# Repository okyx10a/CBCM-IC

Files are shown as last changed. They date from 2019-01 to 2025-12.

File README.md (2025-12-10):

# CBCM-IC Testing Platform
**Full-stack mixed-signal test fixture for Charge-Based Capacitance Measurement ICs**  
Designed, fabricated, and validated at York University (2018–2019)

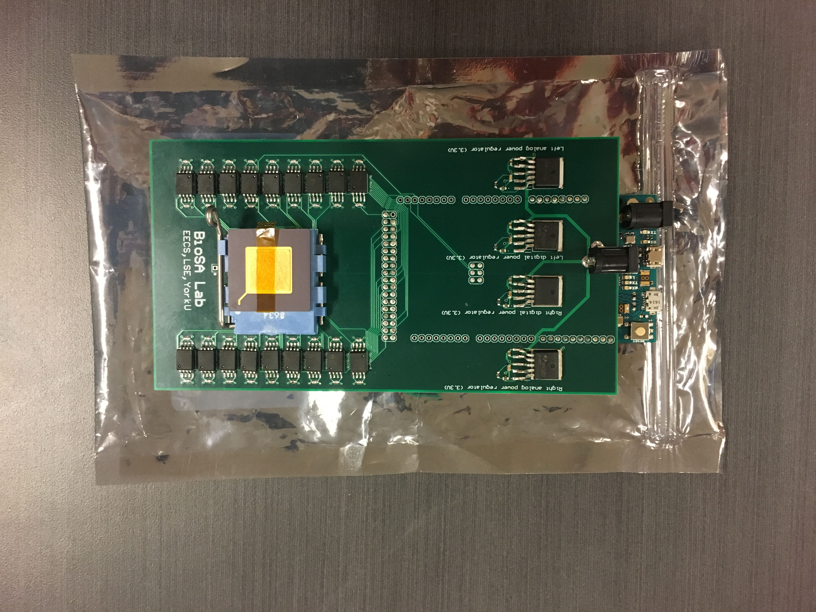
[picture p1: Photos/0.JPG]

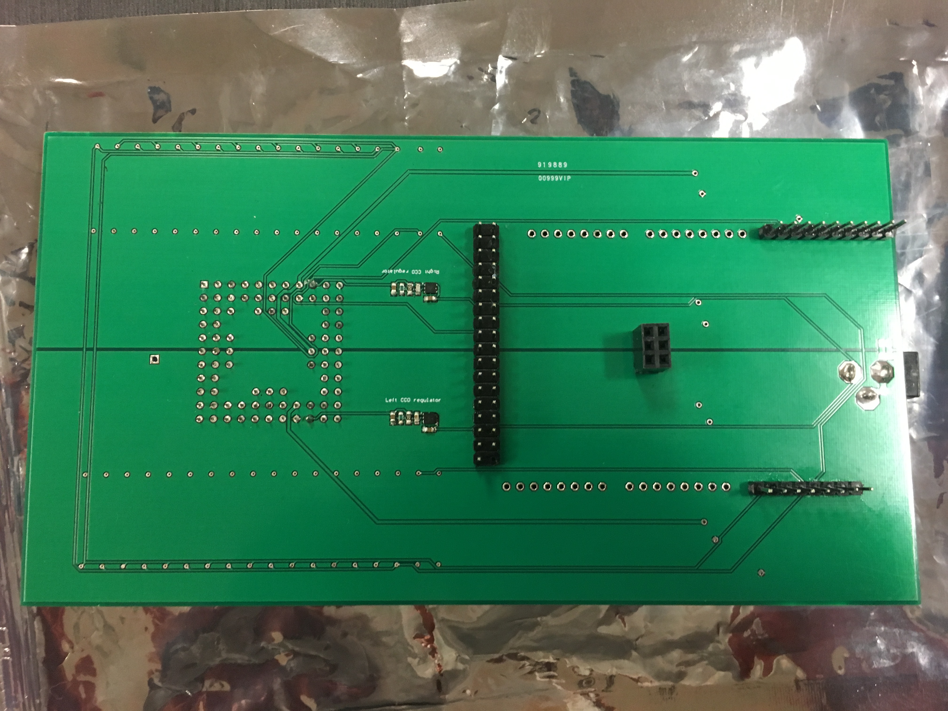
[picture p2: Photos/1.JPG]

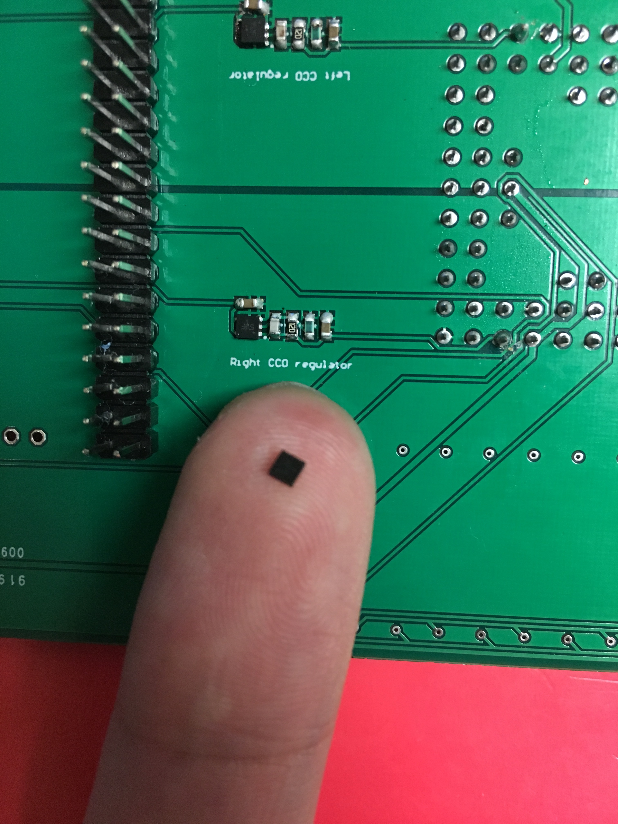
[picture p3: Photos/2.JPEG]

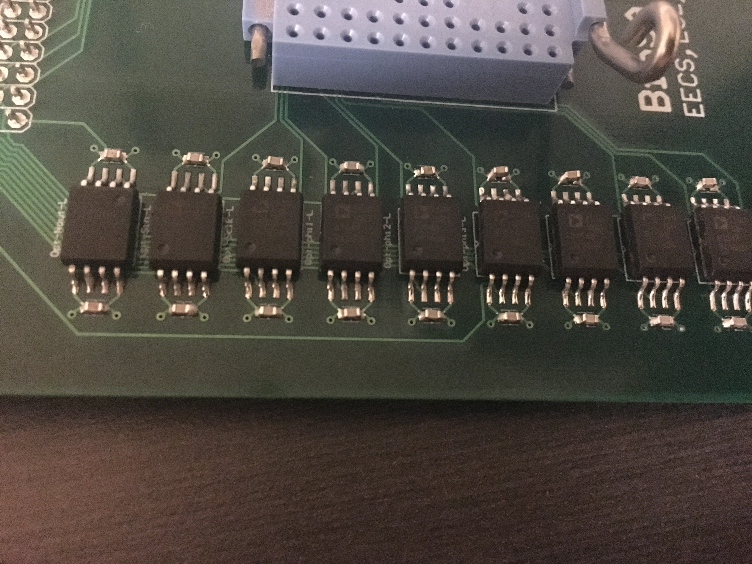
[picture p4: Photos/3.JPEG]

*4-layer mixed-signal test board with separated analog/digital ground planes*

## Directory Structure
├── Hardware/                       → Altium project  
├── Software/                       → Arduino code + PyQt GUI  
├── Photos/                         → Assembly  
├── Test results/                   → Raw data and measurement data  
├── CBCM project summery.docx       → Test fixture construction explanation  
├── Tools chain setup.txt           → Note for succeeding developer  
└── README.md

## Key Features
- 4-layer KiCad design with proper analog/digital ground splitting
- SAM3X8E ARM Cortex-M3 (Arduino Due core) for real-time pattern generation and data acquisition
- Interfaces: SPI (20 MHz), UART
- SMT soldering down to 0603 passives and QFN packages (hand-soldered prototype)
- Automated measurement and data logging via Python + PyQt GUI

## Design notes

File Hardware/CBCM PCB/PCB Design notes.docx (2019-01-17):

1. 0603 seems to be the best size for SMD prototyping.
2. EPAD pin on regulators (TO-263 package) should be connected to ground?
3. The minimal recommended capacitor is 47uF, however the selected capacitor has a (+ -20%) tolerance. Which means it might have a value lower than 47uF. Is that something I should be worried about?
4. The 1.85V regulator is untested on the breadboard I shall record every design detail.

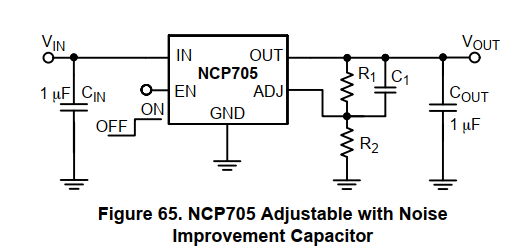
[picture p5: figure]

5. To achieve 1.85V a R2 = 99.048kOhm resistor is needed (while R1 = 130k), however only 98.8kOhm resistor is available on the market. This would result in a 1.8526V output voltage. I wonder if that 0.0026 surplus will be an issue?
6. Data sheet’s note on Cin: It is recommended to connect a minimum of 1uF Ceramic X5R or X7R capacitor close to the IN pin of the device.
7. Data sheet’s note on Cout: The NCP705 requires an output capacitor connected as close as possible to the output pin of the regulator. The minimal capacitor value is 1uF and X7R or X5R dielectric due to its low capacitance variations over the specified temperature range.
8. Data sheet’s note on C1: To improve dynamic performance capacitor C1 should be at least 1 nF. Recommended range of capacity is between 10 nF and 100 nF. Higher value of capacitor C1 increasing start-up time.
9. X5R or X7R are class 2 dielectric capacitors:

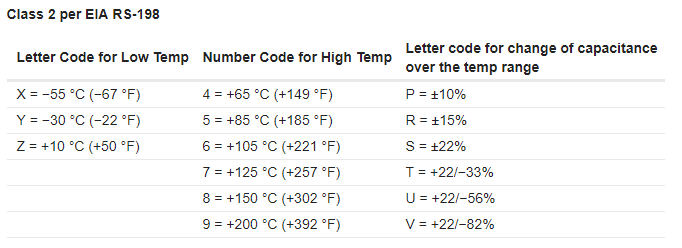
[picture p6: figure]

Details see the following link:

https://forum.digikey.com/t/understanding-ceramic-capacitor-temp-coefficients/727

10. I can’t find the datasheet of the socket I used I have to assume that all pins have a 0.5mm diameter, it should be standardized, but I need to find a way to double check later.
11. The Arduino due has got only one SPI port, which means one side of the IC reading can not be read by Arduino. However, I propose leaving a test pin for that output so that w can directly see its wave form from a logic analyzer.

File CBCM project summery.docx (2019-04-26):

Short description of CBCM project

List of components:

1) CBCM IC
2) Interface PCB
3) Arduino Due
4) Python user interface

CBCM IC

Interface PCB

Arduino Due

Python user interface

Clock, Parameters, data I/O

Power

Digital isolator

Clock, Parameters, data I/O

Parameters, data I/O

Voltage regulators

Data graph, data record files

CBCM IC:

(see CBCM.pdf)

Interface PCB:

The PCB is designed to be an Arduino shield, it provides 4x3.3V power line for left and right digital/analog power respectively. In addition, the PCB also provides 18 digital isolators for electrical isolation of signals input and output signals given by the Arduino board.

Arduino Due:

The Arduino board is responsible for generating required signals and read the IC output. (Detailed I/O can be found in CBCM.pdf)

On the other hand, the board receives instructions from and return the collected data to the python user interface.

Initialization:

1) Generating clock signal
2) Set initial sampling rate
3) Set initial CCO parameter

Work loop:

The loop will be listening for 4 types of instructions

1) Set Sampling rate
2) Set COO parameter
3) Set Calibration input
4) Read IC output

Python user interface:

The python user interface is where we control the test parameters and procedures. It receives the data from and send test configuration commands to Arduino board.

The user interface provides 2 modes for testing:

1) Continuous reading for single calibration value
2) Scanning through all calibration values

In addition, it plots the result data and record the resulting data in a file.

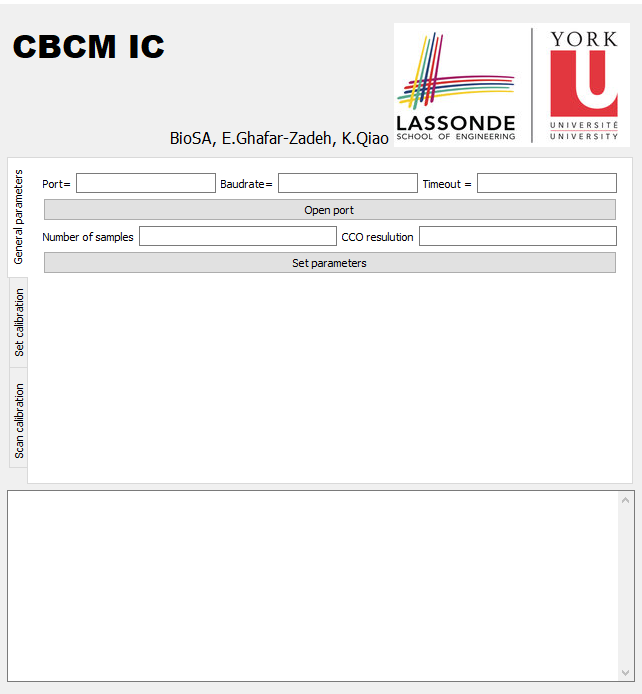
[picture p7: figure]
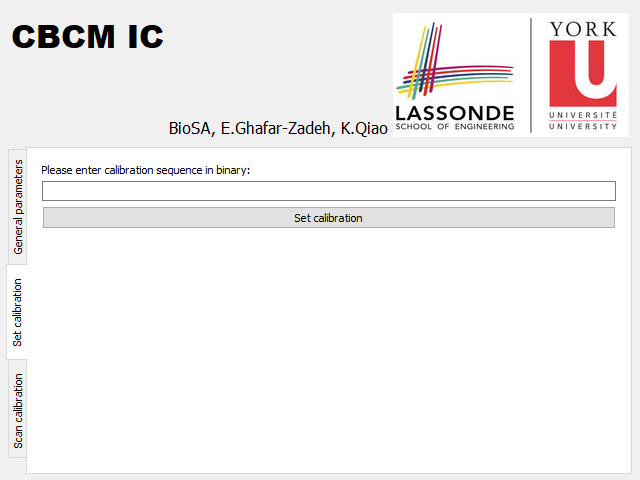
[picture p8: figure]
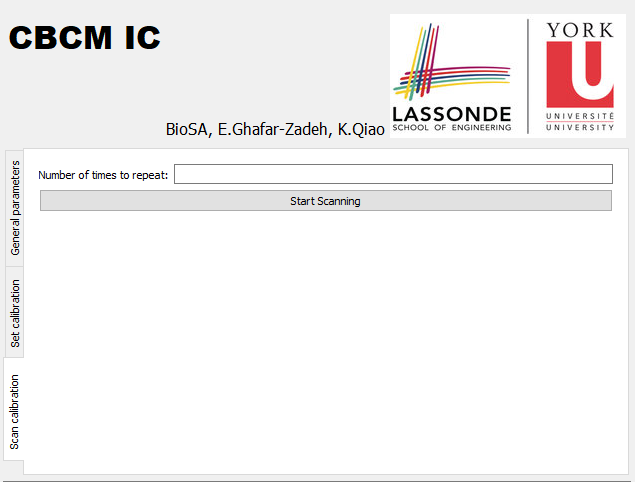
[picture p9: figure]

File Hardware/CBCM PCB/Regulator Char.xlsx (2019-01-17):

left 1.85 | max | mean | note | left analog 3.3 | max | mean
10000 | 1.96 | 1.91 |  | 10000 | 3.4 | 3.36
4700 | 1.96 | 1.91 |  | 4700 | 3.4 | 3.36
3300 | 1.96 | 1.91 |  | 3300 | 3.4 | 3.36
2200 | 1.96 | 1.91 |  | 2200 | 3.4 | 3.36
1000 | 1.96 | 1.91 |  | 1000 | 3.4 | 3.36
680 | 1.96 | 1.91 |  | 680 | 3.4 | 3.37
470 | 1.96 | 1.91 |  | 470 | 3.4 | 3.37
330 | 1.96 | 1.91 |  | 330 | 3.4 | 3.36
220 | 1.96 | 1.91 |  | 220 | 3.4 | 3.36
100 | 1.96 | 1.91 |  | 100 | 3.4 | 3.36
 |  |  |  | 47 | 3.4 | 3.36
 |  |  |  | 10 | 3.44 | 3.35
 |  |  |  | 4.7 |  |  | resistor heat up cancel test point
right 1.85 |  |  |  | left digital 3.3
10000 | 1.96 | 1.91 |  | 10000 | 3.4 | 3.35
4700 | 1.96 | 1.91 |  | 4700 | 3.4 | 3.35
3300 | 1.96 | 1.91 |  | 3300 | 3.4 | 3.35
2200 | 1.96 | 1.91 |  | 2200 | 3.4 | 3.35
1000 | 1.96 | 1.91 |  | 1000 | 3.4 | 3.35
680 | 1.96 | 1.91 |  | 680 | 3.4 | 3.35
470 | 1.96 | 1.91 |  | 470 | 3.4 | 3.35
330 | 1.96 | 1.91 |  | 330 | 3.4 | 3.35
220 | 1.96 | 1.91 |  | 220 | 3.4 | 3.35
100 | 1.96 | 1.91 |  | 100 | 3.4 | 3.35
 |  |  |  | 47 | 3.4 | 3.35
 |  |  |  | 10 | 3.44 | 3.34
 |  |  |  | 4.7 |  |  | resistor heat up cancel test point
 |  |  |  | right digital 3.3
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

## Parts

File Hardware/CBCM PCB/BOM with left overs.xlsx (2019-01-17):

Designator | Quantity | Digi-Key_Purchase_URL | Manufacturer Part Number | left amount
C1, C2, C26, C27 | 4 | https://www.digikey.ca/product-detail/en/samsung-electro-mechanics/CL10A476MR8NZNE/1276-6528-1-ND/5961387 | CL10A476MR8NZNE | 6
C3, C4, C5, C6, C28, C29, C30, C31 | 8 | https://www.digikey.ca/product-detail/en/murata-electronics-north-america/GRM188R60J105KA01D/490-1550-1-ND/587755 | GRM188R60J105KA01D | 24
C7, C8, C9, C10, C11, C12, C13, C14, C15, C16, C17, C18, C19, C20, C21, C22, C23, C24, C25, C32, C33, C34, C35, C36, C37, C38, C39, C40, C41, C42, C43, C44, C45, C46, C47, C48, C49, C50 | 38 | https://www.digikey.ca/product-detail/en/murata-electronics-north-america/GCM188R72A103KA37J/490-8028-1-ND/4380313 | GCM188R72A103KA37J | 162
CBCM IC | 1 | https://www.ebay.ca/itm/NEW-AMP-1PC-55381-6-CONN-SOCKET-SKT-ZIF-PGA-BURNIN-SIZE-85-POS-Handle-lever/253246908054?epid=14008858492 | PGA85 socket | 1
J1 | 1
Left analog power regulator (3.3V), Left digital power regulator (3.3V), Right analog power regulator (3.3V), Right digital power regulator (3.3V) | 4 | https://www.digikey.ca/product-detail/en/texas-instruments/TPS75901KTTR/296-29784-1-ND/2769170 | TPS75901KTTR | 6
Left CCO regulator, Right CCO regulator | 2 | https://www.digikey.ca/product-detail/en/on-semiconductor/NCP705MTADJTCG/NCP705MTADJTCGOSCT-ND/8538627 | NCP705MTADJTCG | 8
Opt-G1-L, Opt-G1-R, Opt-G2-L, Opt-G2-R, Opt-G3-L, Opt-G3-R, Opt-Nout-L, Opt-Nout-R, Opt-phi1-L, Opt-phi1-R, Opt-phi2-L, Opt-phi2-R, Opt-phi3-L, Opt-phi3-R, Opt-Sclk-L, Opt-Sclk-R, Opt-Sin-L, Opt-Sin-R | 18 | https://www.digikey.ca/product-detail/en/analog-devices-inc/ADUM210N1BRIZ/ADUM210N1BRIZ-ND/6072296 | ADUM210N1BRIZ | 4
POWER | 1
PWMH | 1
R1, R3, R7, R9 | 4 | https://www.digikey.ca/product-detail/en/susumu/RR0816P-513-D/RR08P51.0KDCT-ND/432765 | RR0816P-513-D | 96
R2, R4, R8, R10 | 4 | https://www.digikey.ca/product-detail/en/RT0603BRD0730K1L/YAG1631CT-ND/5139079/?itemSeq=277251875 | RT0603BRD0730K1L | 6
R5, R11 | 2 | https://www.digikey.ca/product-detail/en/yageo/RC0603FR-07130KL/311-130KHRCT-ND/729882 | RC0603FR-07130KL | 102
R6, R12 | 2 | https://www.mouser.ca/ProductDetail/KOA-Speer/RN731JTTD9882F100?qs=sGAEpiMZZMu61qfTUdNhG4HwY6bMI5JU0LoUBqLeusY%3d | RN731JTTD9882F100 | 83
SPI | 1
X2 | 1
XIO | 1

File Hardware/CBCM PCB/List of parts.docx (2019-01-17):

## Materials and links

TPS75901KTTR (3.3 regulator)

https://www.digikey.ca/product-detail/en/texas-instruments/TPS75901KTTR/296-29784-1-ND/2769170

ACPL-072L-500E (opto-coupler)

https://www.digikey.ca/product-detail/en/broadcom-limited/ACPL-072L-500E/516-3131-1-ND/4969461?utm_source=snapeda&utm_medium=aggregator&utm_campaign=symbol

GRM188R60G476ME15D (47uF Cap)

https://www.digikey.ca/product-detail/en/murata-electronics-north-america/GRM188R60G476ME15D/490-13246-1-ND/5877454?utm_source=snapeda&utm_medium=aggregator&utm_campaign=symbol

RR0816P-513-D (51k Res)

https://www.digikey.ca/product-detail/en/susumu/RR0816P-513-D/RR08P51.0KDCT-ND/432765

RT0603BRD0730K1L (30.1k Res)

https://www.digikey.ca/product-detail/en/yageo/RT0603BRD0730K1L/YAG1631CT-ND/5139079

NCP705MTADJTCG (1.85 regulator)

https://www.digikey.ca/product-detail/en/on-semiconductor/NCP705MTADJTCG/NCP705MTADJTCGOSCT-ND/8538627

GRM188R60J105KA01D (1uF Cap)

https://www.digikey.ca/product-detail/en/murata-electronics-north-america/GRM188R60J105KA01D/490-1550-1-ND/587755

ERJ-3GEY0R00V (98.8k Res)

https://www.digikey.ca/product-detail/en/panasonic-electronic-components/ERJ-3GEY0R00V/P0.0GCT-ND/134711

RC0603FR-07130KL (130k Res)

https://www.digikey.ca/product-detail/en/yageo/RC0603FR-07130KL/311-130KHRCT-ND/729882

GRM1885C1H103JA01D (10nF Cap)

https://www.digikey.ca/product-detail/en/murata-electronics-north-america/GRM1885C1H103JA01D/490-9666-1-ND/4934772?utm_source=snapeda&utm_medium=aggregator&utm_campaign=symbol

1x8 male header x5

1x10 male header x1

18x2 male header x1

3x2 female header x1

Haven’t search up the links for headers yet, but they should be pretty common..

DC21MMX

DC Barrel power jack

Left half of the chip:

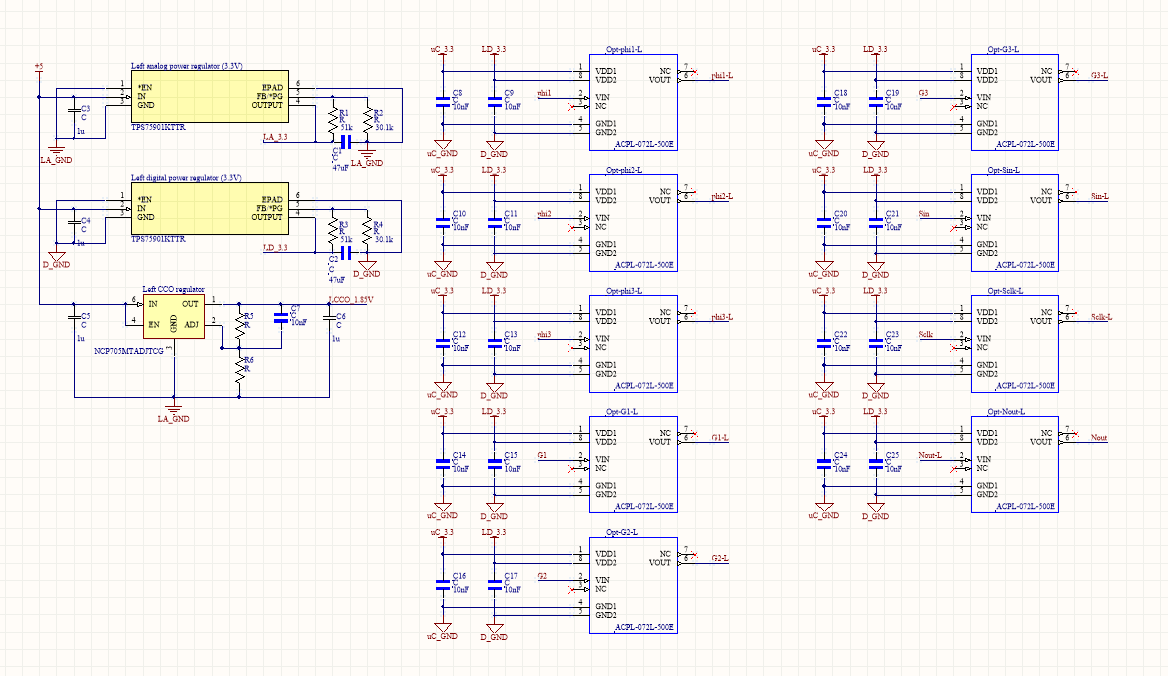
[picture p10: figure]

Right half of the chip:

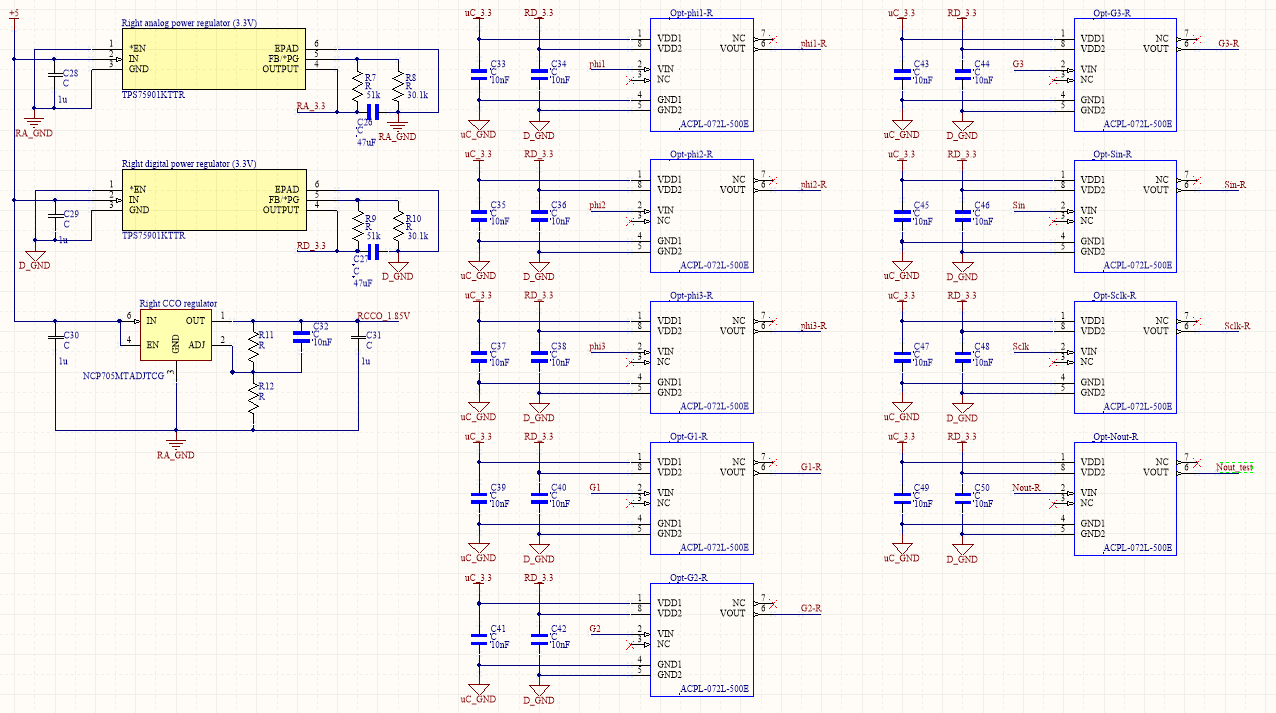
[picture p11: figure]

Common part

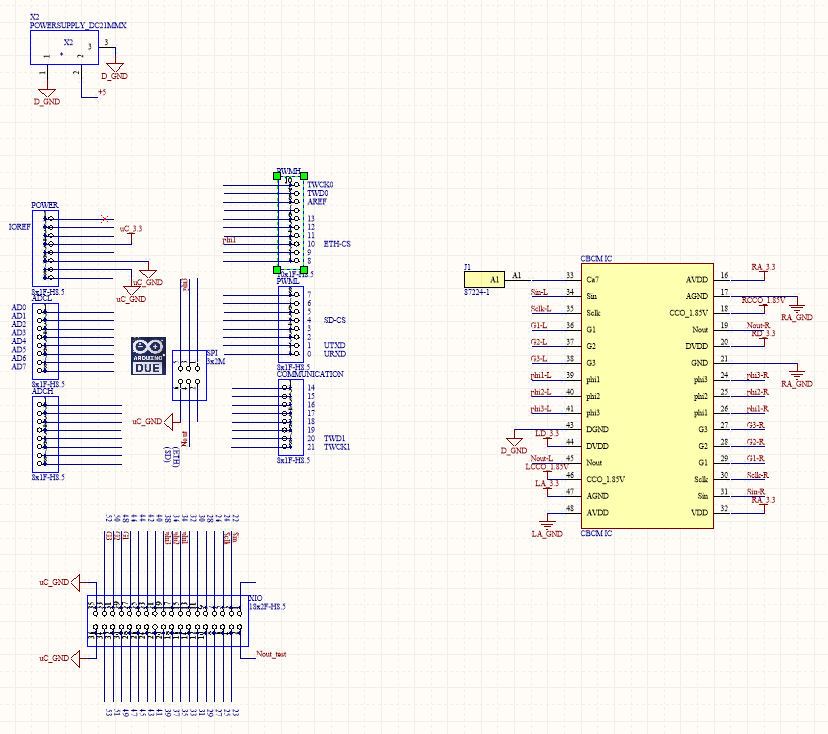
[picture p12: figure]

PCB layout:

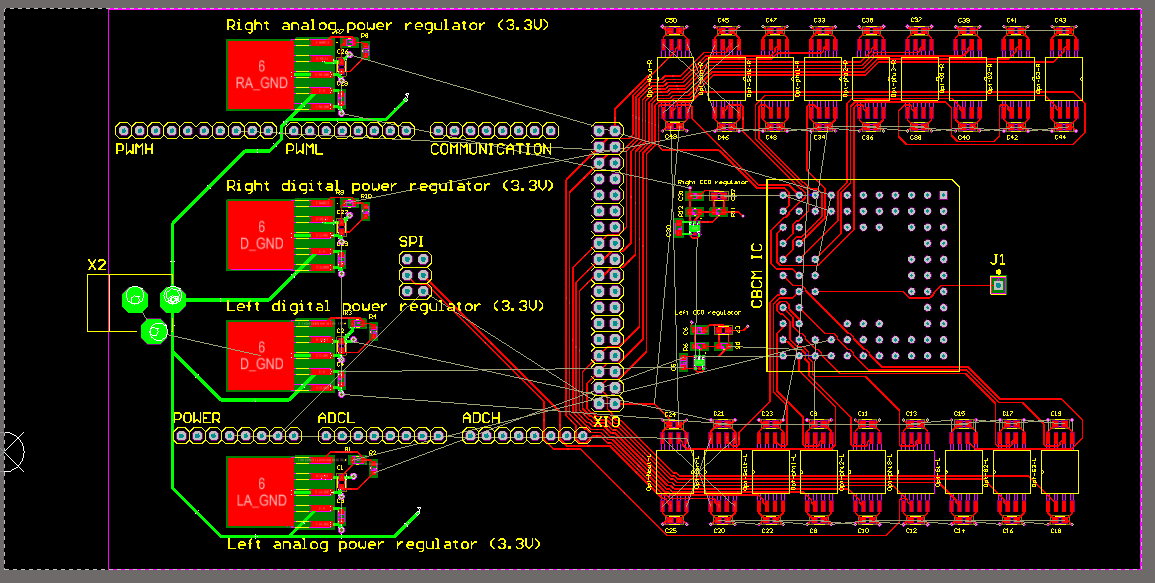
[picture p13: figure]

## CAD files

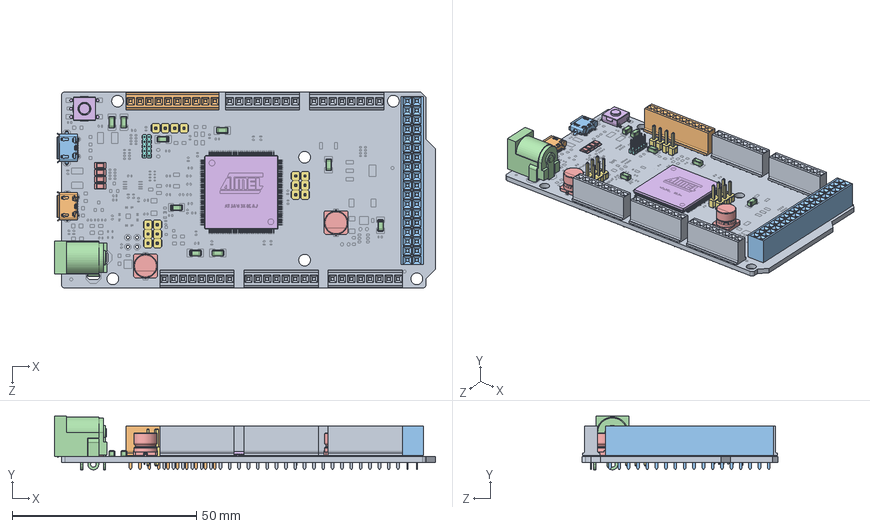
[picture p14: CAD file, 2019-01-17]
Hardware/CBCM PCB/arduino-due-1.snapshot.10/ARDUINO DUE.SLDASM
103.5 x 14.6 x 53.3 mm
PCB - Arduino
MicroUSB B - Hirose - ZX62D-B-5P8
MicroUSB AB - Hirose - ZX62D-AB-5P8
Power Jack - Kycon - KLDHCX-0202-A
LED - Kingbright - KPT-3216EC x 4
Microchip - Atmel - SAM3X8EAU
Berg Header - 2.54 x 2 x 8
Berg Header - 1.27 x 10
Berg Header Receptacle 2.54 x 8 - FCI - 66951-008LF x 5
Berg Header Receptacle 2.54 x 10 - FCI - 66951-010LF
Berg Header Receptacle 2.54 x 36 - FCI - 66953-018LF
Capacitor x 9
Capacitor - Nichicon - UUR1C101MCL1GS x 2
Switch - ESwitch - TLE3303

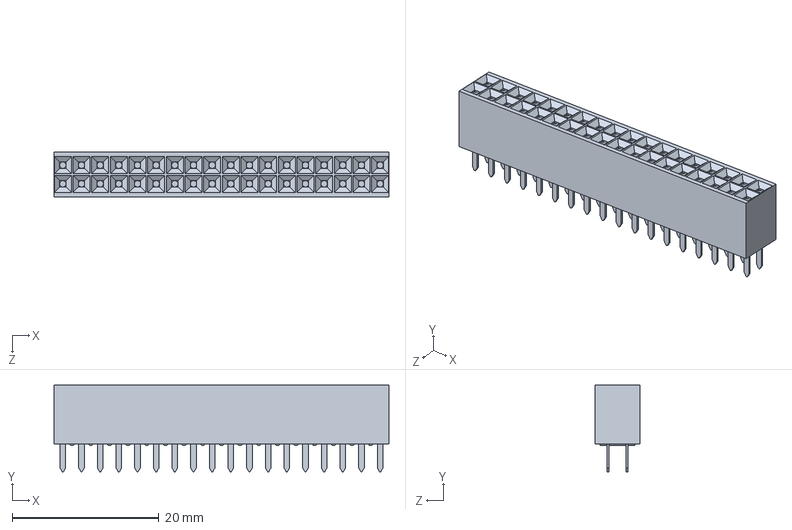
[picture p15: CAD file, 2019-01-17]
Hardware/CBCM PCB/arduino-due-1.snapshot.10/Arduino Due/Berg Header Receptacle 2.54 x 36 - FCI - 66953-018LF.SLDPRT
45.6 x 11.8 x 6.10 mm

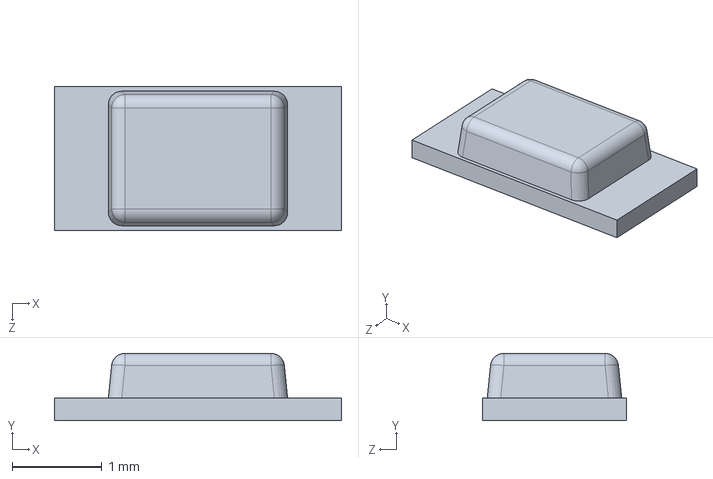
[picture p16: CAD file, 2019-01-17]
Hardware/CBCM PCB/arduino-due-1.snapshot.10/Arduino Due/LED - Kingbright - KPT-3216EC.SLDPRT
3.20 x 0.75 x 1.60 mm

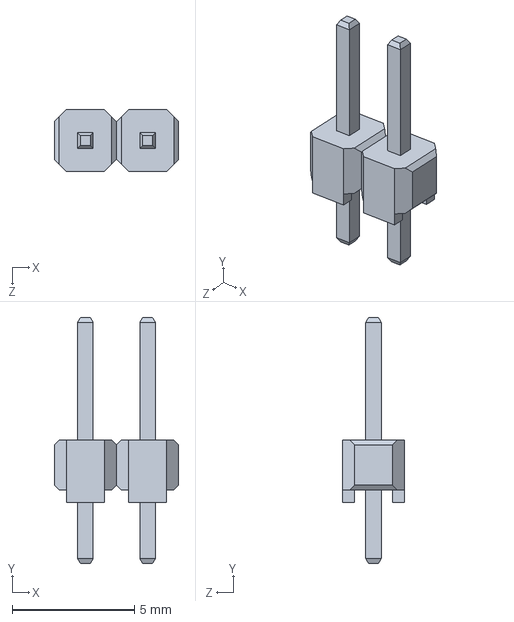
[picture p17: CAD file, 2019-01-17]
Hardware/CBCM PCB/arduino-due-1.snapshot.10/Arduino Due/Berg Header - 2.54 x 2.SLDPRT
5.08 x 10.0 x 2.54 mm

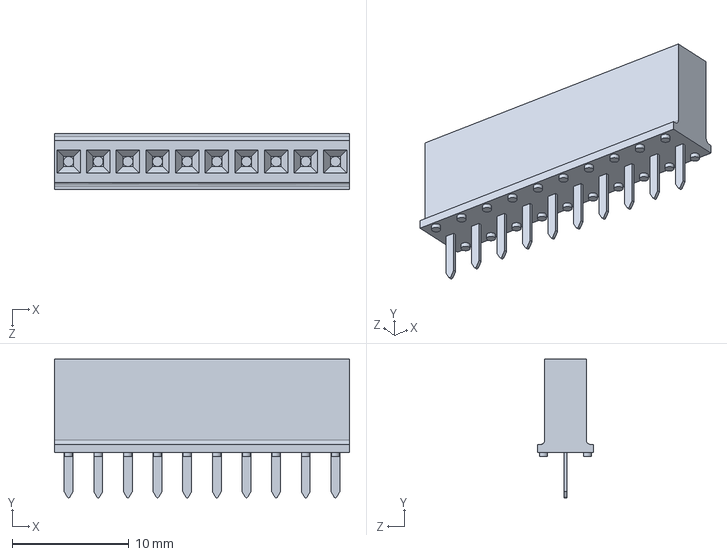
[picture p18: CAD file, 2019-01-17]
Hardware/CBCM PCB/arduino-due-1.snapshot.10/Arduino Due/Berg Header Receptacle 2.54 x 10 - FCI - 66951-010LF.SLDPRT
25.3 x 11.9 x 4.78 mm

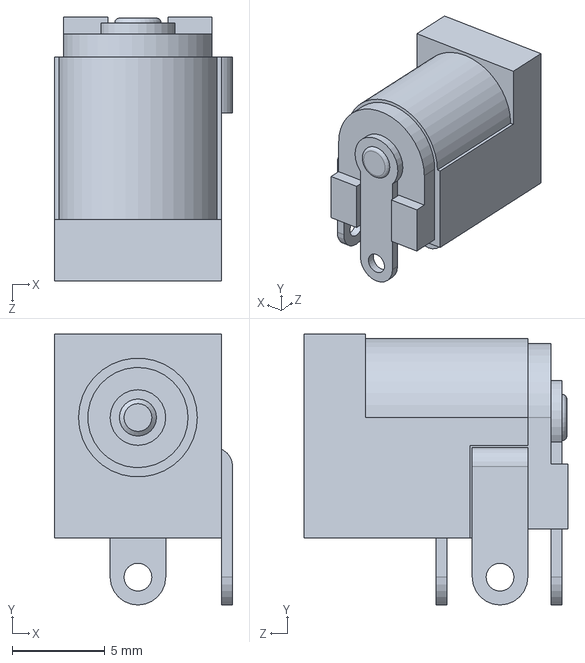
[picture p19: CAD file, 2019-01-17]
Hardware/CBCM PCB/arduino-due-1.snapshot.10/Arduino Due/Power Jack - Kycon - KLDHCX-0202-A.SLDPRT
9.60 x 14.6 x 14.2 mm

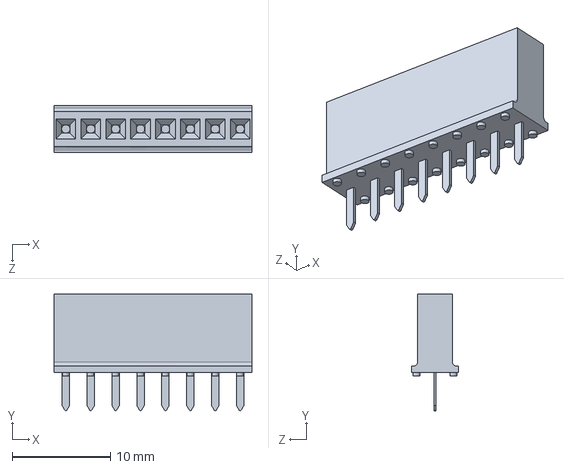
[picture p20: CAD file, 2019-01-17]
Hardware/CBCM PCB/arduino-due-1.snapshot.10/Arduino Due/Berg Header Receptacle 2.54 x 8 - FCI - 66951-008LF.SLDPRT
20.2 x 11.9 x 4.78 mm

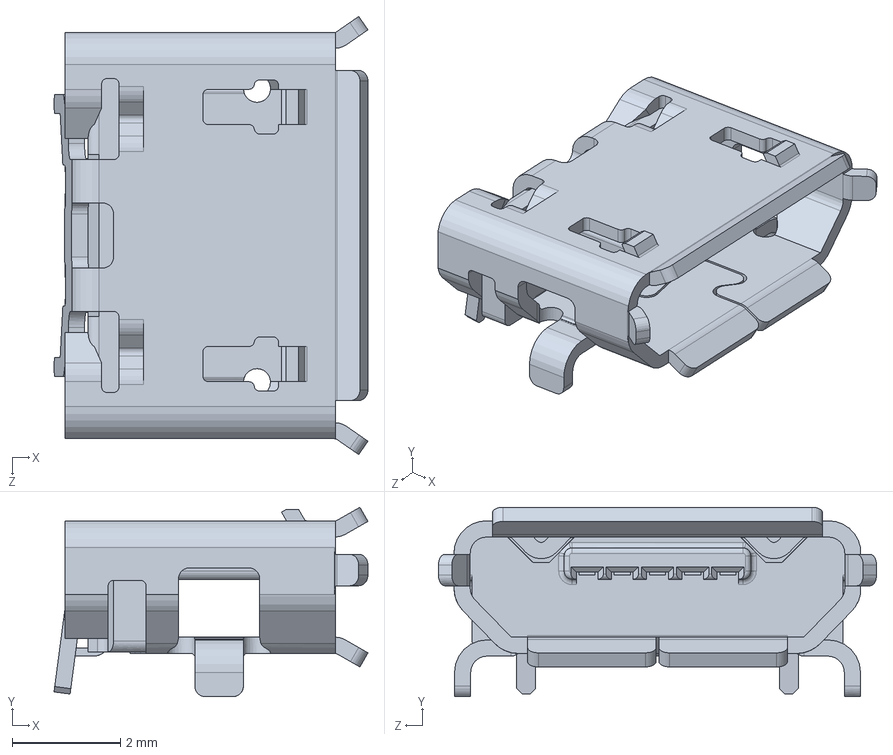
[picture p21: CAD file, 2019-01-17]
Hardware/CBCM PCB/arduino-due-1.snapshot.10/Arduino Due/MicroUSB B - Hirose - ZX62D-B-5P8.SLDPRT
5.80 x 3.50 x 8.09 mm

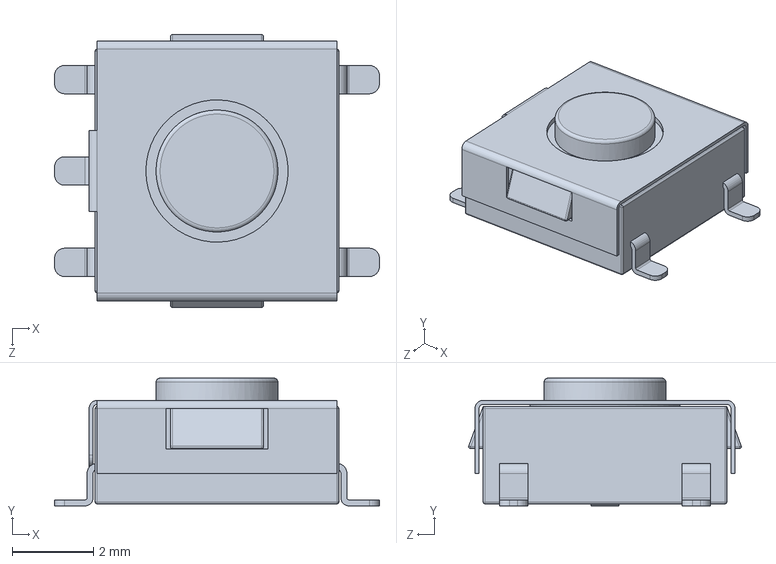
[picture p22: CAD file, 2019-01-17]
Hardware/CBCM PCB/arduino-due-1.snapshot.10/Arduino Due/Switch - ESwitch - TLE3303.SLDPRT
8.00 x 3.15 x 6.71 mm

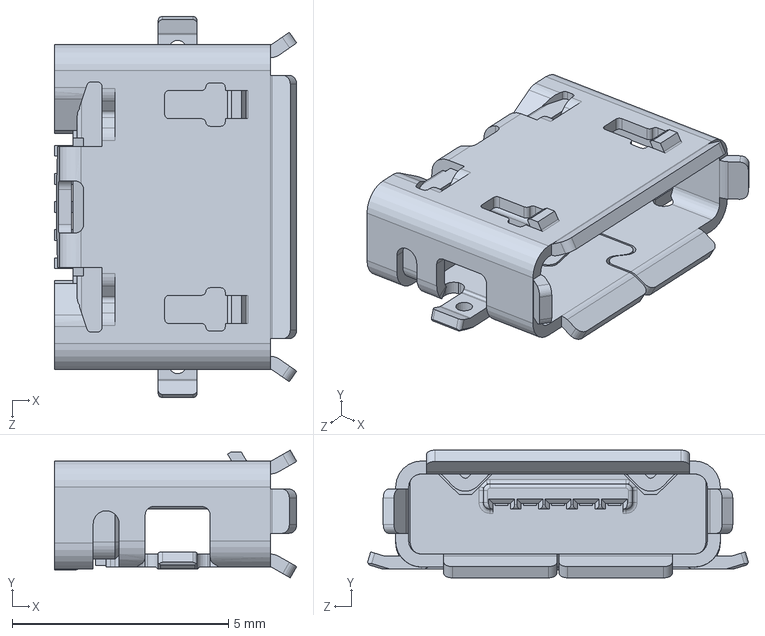
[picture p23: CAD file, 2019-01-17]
Hardware/CBCM PCB/arduino-due-1.snapshot.10/Arduino Due/MicroUSB AB - Hirose - ZX62-AB-5PA.SLDPRT
5.60 x 2.95 x 8.80 mm

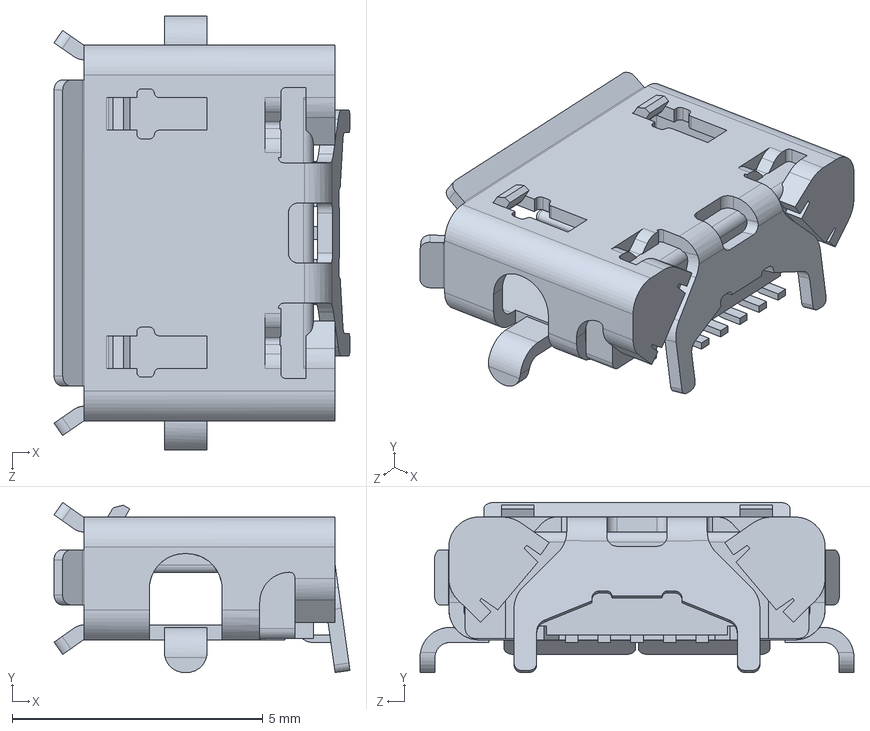
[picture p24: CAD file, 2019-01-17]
Hardware/CBCM PCB/arduino-due-1.snapshot.10/Arduino Due/MicroUSB AB - Hirose - ZX62D-AB-5P8.SLDPRT
5.90 x 3.39 x 8.65 mm

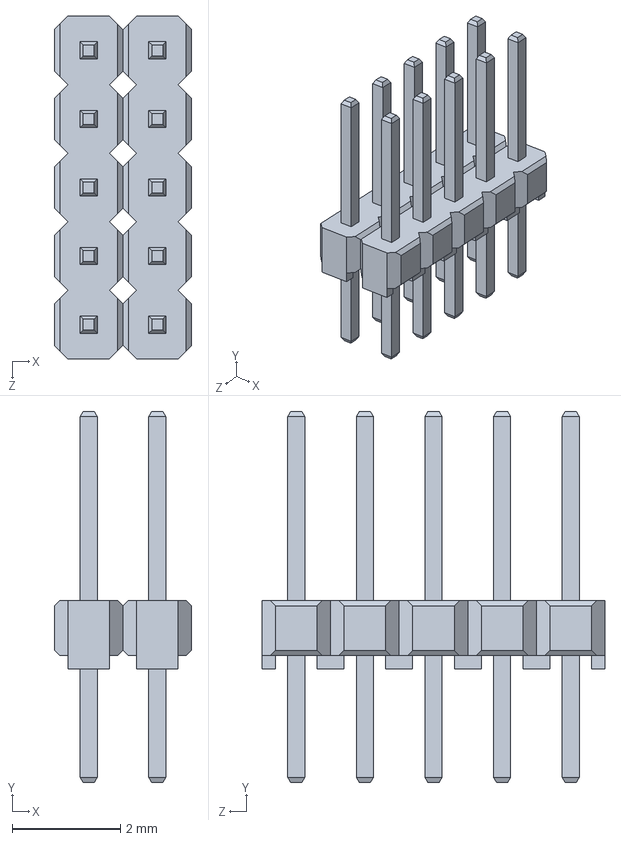
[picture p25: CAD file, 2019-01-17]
Hardware/CBCM PCB/arduino-due-1.snapshot.10/Arduino Due/Berg Header - 1.27 x 10.SLDPRT
2.54 x 6.88 x 6.35 mm

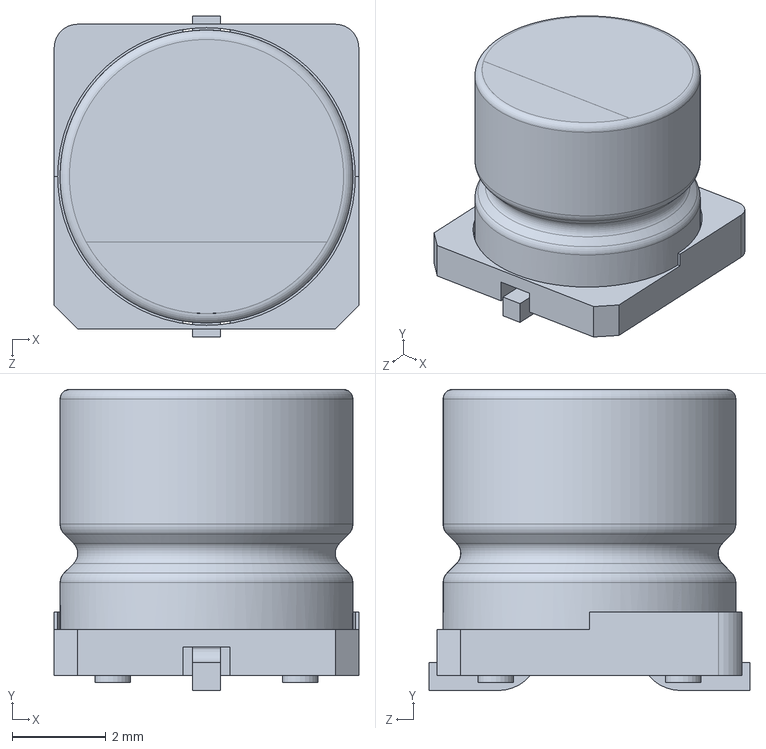
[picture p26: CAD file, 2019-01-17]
Hardware/CBCM PCB/arduino-due-1.snapshot.10/Arduino Due/Capacitor - Nichicon - UUR1C101MCL1GS.SLDPRT
6.50 x 6.42 x 6.85 mm

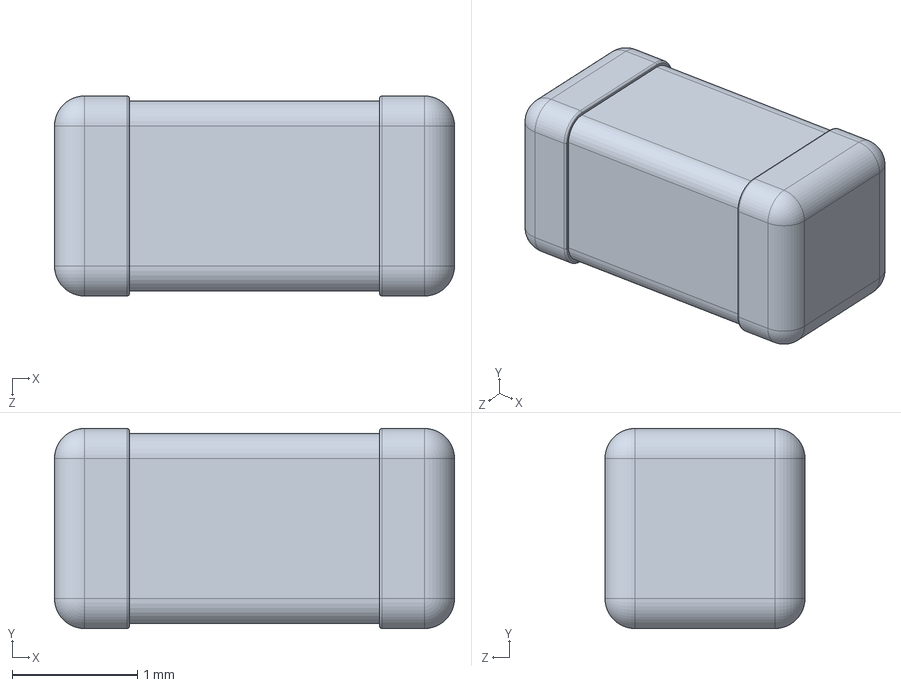
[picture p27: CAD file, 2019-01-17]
Hardware/CBCM PCB/arduino-due-1.snapshot.10/Arduino Due/Capacitor.SLDPRT
3.20 x 1.60 x 1.60 mm

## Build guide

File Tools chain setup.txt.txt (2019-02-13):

Here's the git hub link of the CBCM project: https://github.com/okyx10a/CBCM-IC.git
Custom PCB design files will be found in directory: /Hardware/CBCM PCB
Design tool :Altium Designer

For programming the microcontroller:
Arduino IDE: https://www.arduino.cc/en/main/software
Guide on how to set up Arduino Due: https://www.arduino.cc/en/Guide/ArduinoDue
Due's microcontroller datasheet:SAM3X datasheet
Pin mapping for the microcontroller to board layout:Pin mapping

For the running the interface program:
Python: https://www.python.org/downloads/
To install various python packages you will need: pip it's basically a package manager
Additional python packages: 
pyserial (for USB communication)
numpy, scipy, matplot (they make python work like Matlab)
pyqt5 (For GUI I'm currently working on)

Optional tools:
To unlock the full potential of the microcontroller I would recommend Atmel Studio together with Microchip® Advanced Software Framework. They are way more professional however totally optional. 
For debugging serial port: RealTerm 
For version control with GitHub: Sourcetree or Github desktop
Check out this website for documentation and other useful math packages as well: https://scipy.org/

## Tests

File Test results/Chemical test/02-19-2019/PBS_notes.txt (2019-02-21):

graph becomes a straight line after PBS evaporates;
the solution leaving black remainents on top of chip
there was a time where read out was almost zero, problem solved by powerdown and then power up the chip, it is suspected that it was a side effect of the PBS

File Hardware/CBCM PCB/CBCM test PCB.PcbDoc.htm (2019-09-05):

Reporting Options

# File in Previous Format

Date | : | 2019/8/9
Time | : | 17:27:15
Filename | : | E:\Owen\Documents\Bio sensor chip\CBCM IC\CBCM-IC\Hardware\CBCM PCB\CBCM test PCB.PcbDoc

Version | Warning

This file was generated by an earlier version of the software

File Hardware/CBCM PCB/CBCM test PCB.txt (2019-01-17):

Field=Quantity~Integer~Quantity~385|Field=Digi-Key_Purchase_URL~String~Digi-Key_Purchase_URL~270|Field=Manufacturer Part Number~String~Manufacturer Part Number~219|ReportField=Currency~<none>|ReportField=ProductionQuantity~1|ReportField=ProjectFileName~CBCM test PCB.PrjPCB|ReportField=ProjectFullPath~E:\Owen\Documents\Bio sensor chip\CBCM PCB\CBCM test PCB.PrjPCB|ReportField=Title~Bill of Materials For Project [CBCM test PCB.PrjPCB] (No PCB Document Selected)|ReportField=TotalQuantity~93|ReportField=ReportTime~18:18:21|ReportField=ReportDate~2018/10/29|ReportField=ReportDateTime~2018/10/29 18:18:21|ReportField=OutputName~Bill of Materials|ReportField=OutputType~BOM_PartType|ReportField=GeneratorName~BOM|ReportField=GeneratorDescription~Bill of Materials|ReportField=VariantName~None|ReportField=Address1~|ReportField=Address2~|ReportField=Address3~|ReportField=Address4~|ReportField=ApprovedBy~|ReportField=Author~|ReportField=CheckedBy~|ReportField=CompanyName~|ReportField=CurrentDate~2018/10/29|ReportField=CurrentTime~18:16:47|ReportField=Date~|ReportField=DocumentFullPathAndName~E:\Owen\Documents\Bio sensor chip\CBCM PCB\IC common.SchDoc|ReportField=DocumentName~IC common.SchDoc|ReportField=DocumentNumber~|ReportField=DrawnBy~|ReportField=Engineer~|ReportField=ImagePath~|ReportField=ModifiedDate~2018/10/26|ReportField=Organization~|ReportField=ProjectName~CBCM test PCB.PrjPCB|ReportField=Revision~|ReportField=Rule~|ReportField=SheetNumber~|ReportField=SheetTotal~|ReportField=Time~|ReportField=Title~|ReportField=DataSourceFileName~CBCM test PCB.PrjPCB|ReportField=DataSourceFullPath~E:\Owen\Documents\Bio sensor chip\CBCM PCB\CBCM test PCB.PrjPCB
42|https://www.digikey.ca/product-detail/en/murata-electronics-north-america/GRM188R60G476ME15D/490-13246-1-ND/5877454?utm_source=snapeda&utm_medium=aggregator&utm_campaign=symbol, https://www.digikey.ca/product-detail/en/murata-electronics-north-america/GRM188R60G476ME15D/490-13246-1-ND/5877454?utm_source=snapeda&utm_medium=aggregator&utm_campaign=symbol, https://www.digikey.ca/product-detail/en/murata-electronics-north-america/GRM1885C1H103JA01D/490-9666-1-ND/4934772?utm_source=snapeda&utm_medium=aggregator&utm_campaign=symbol, https://www.digikey.ca/product-detail/en/murata-electronics-north-america/GRM1885C1H103JA01D/490-9666-1-ND/4934772?utm_source=snapeda&utm_medium=aggregator&utm_campaign=symbol, https://www.digikey.ca/product-detail/en/murata-electronics-north-america/GRM1885C1H103JA01D/490-9666-1-ND/4934772?utm_source=snapeda&utm_medium=aggregator&utm_campaign=symbol, https://www.digikey.ca/product-detail/en/murata-electronics-north-america/GRM1885C1H103JA01D/490-9666-1-ND/4934772?utm_source=snapeda&utm_medium=aggregator&utm_campaign=symbol, https://www.digikey.ca/product-detail/en/murata-electronics-north-america/GRM1885C1H103JA01D/490-9666-1-ND/4934772?utm_source=snapeda&utm_medium=aggregator&utm_campaign=symbol, https://www.digikey.ca/product-detail/en/murata-electronics-north-america/GRM1885C1H103JA01D/490-9666-1-ND/4934772?utm_source=snapeda&utm_medium=aggregator&utm_campaign=symbol, https://www.digikey.ca/product-detail/en/murata-electronics-north-america/GRM1885C1H103JA01D/490-9666-1-ND/4934772?utm_source=snapeda&utm_medium=aggregator&utm_campaign=symbol, https://www.digikey.ca/product-detail/en/murata-electronics-north-america/GRM1885C1H103JA01D/490-9666-1-ND/4934772?utm_source=snapeda&utm_medium=aggregator&utm_campaign=symbol, https://www.digikey.ca/product-detail/en/murata-electronics-north-america/GRM1885C1H103JA01D/490-9666-1-ND/4934772?utm_source=snapeda&utm_medium=aggregator&utm_campaign=symbol, https://www.digikey.ca/product-detail/en/murata-electronics-north-america/GRM1885C1H103JA01D/490-9666-1-ND/4934772?utm_source=snapeda&utm_medium=aggregator&utm_campaign=symbol, https://www.digikey.ca/product-detail/en/murata-electronics-north-america/GRM1885C1H103JA01D/490-9666-1-ND/4934772?utm_source=snapeda&utm_medium=aggregator&utm_campaign=symbol, https://www.digikey.ca/product-detail/en/murata-electronics-north-america/GRM1885C1H103JA01D/490-9666-1-ND/4934772?utm_source=snapeda&utm_medium=aggregator&utm_campaign=symbol, https://www.digikey.ca/product-detail/en/murata-electronics-north-america/GRM1885C1H103JA01D/490-9666-1-ND/4934772?utm_source=snapeda&utm_medium=aggregator&utm_campaign=symbol, https://www.digikey.ca/product-detail/en/murata-electronics-north-america/GRM1885C1H103JA01D/490-9666-1-ND/4934772?utm_source=snapeda&utm_medium=aggregator&utm_campaign=symbol, https://www.digikey.ca/product-detail/en/murata-electronics-north-america/GRM1885C1H103JA01D/490-9666-1-ND/4934772?utm_source=snapeda&utm_medium=aggregator&utm_campaign=symbol, https://www.digikey.ca/product-detail/en/murata-electronics-north-america/GRM1885C1H103JA01D/490-9666-1-ND/4934772?utm_source=snapeda&utm_medium=aggregator&utm_campaign=symbol, https://www.digikey.ca/product-detail/en/murata-electronics-north-america/GRM1885C1H103JA01D/490-9666-1-ND/4934772?utm_source=snapeda&utm_medium=aggregator&utm_campaign=symbol, https://www.digikey.ca/product-detail/en/murata-electronics-north-america/GRM1885C1H103JA01D/490-9666-1-ND/4934772?utm_source=snapeda&utm_medium=aggregator&utm_campaign=symbol, https://www.digikey.ca/product-detail/en/murata-electronics-north-america/GRM1885C1H103JA01D/490-9666-1-ND/4934772?utm_source=snapeda&utm_medium=aggregator&utm_campaign=symbol, https://www.digikey.ca/product-detail/en/murata-electronics-north-america/GRM188R60G476ME15D/490-13246-1-ND/5877454?utm_source=snapeda&utm_medium=aggregator&utm_campaign=symbol, https://www.digikey.ca/product-detail/en/murata-electronics-north-america/GRM188R60G476ME15D/490-13246-1-ND/5877454?utm_source=snapeda&utm_medium=aggregator&utm_campaign=symbol, https://www.digikey.ca/product-detail/en/murata-electronics-north-america/GRM1885C1H103JA01D/490-9666-1-ND/4934772?utm_source=snapeda&utm_medium=aggregator&utm_campaign=symbol, https://www.digikey.ca/product-detail/en/murata-electronics-north-america/GRM1885C1H103JA01D/490-9666-1-ND/4934772?utm_source=snapeda&utm_medium=aggregator&utm_campaign=symbol, https://www.digikey.ca/product-detail/en/murata-electronics-north-america/GRM1885C1H103JA01D/490-9666-1-ND/4934772?utm_source=snapeda&utm_medium=aggregator&utm_campaign=symbol, https://www.digikey.ca/product-detail/en/murata-electronics-north-america/GRM1885C1H103JA01D/490-9666-1-ND/4934772?utm_source=snapeda&utm_medium=aggregator&utm_campaign=symbol, https://www.digikey.ca/product-detail/en/murata-electronics-north-america/GRM1885C1H103JA01D/490-9666-1-ND/4934772?utm_source=snapeda&utm_medium=aggregator&utm_campaign=symbol, https://www.digikey.ca/product-detail/en/murata-electronics-north-america/GRM1885C1H103JA01D/490-9666-1-ND/4934772?utm_source=snapeda&utm_medium=aggregator&utm_campaign=symbol, https://www.digikey.ca/product-detail/en/murata-electronics-north-america/GRM1885C1H103JA01D/490-9666-1-ND/4934772?utm_source=snapeda&utm_medium=aggregator&utm_campaign=symbol, https://www.digikey.ca/product-detail/en/murata-electronics-north-america/GRM1885C1H103JA01D/490-9666-1-ND/4934772?utm_source=snapeda&utm_medium=aggregator&utm_campaign=symbol, https://www.digikey.ca/product-detail/en/murata-electronics-north-america/GRM1885C1H103JA01D/490-9666-1-ND/4934772?utm_source=snapeda&utm_medium=aggregator&utm_campaign=symbol, https://www.digikey.ca/product-detail/en/murata-electronics-north-america/GRM1885C1H103JA01D/490-9666-1-ND/4934772?utm_source=snapeda&utm_medium=aggregator&utm_campaign=symbol, https://www.digikey.ca/product-detail/en/murata-electronics-north-america/GRM1885C1H103JA01D/490-9666-1-ND/4934772?utm_source=snapeda&utm_medium=aggregator&utm_campaign=symbol, https://www.digikey.ca/product-detail/en/murata-electronics-north-america/GRM1885C1H103JA01D/490-9666-1-ND/4934772?utm_source=snapeda&utm_medium=aggregator&utm_campaign=symbol, https://www.digikey.ca/product-detail/en/murata-electronics-north-america/GRM1885C1H103JA01D/490-9666-1-ND/4934772?utm_source=snapeda&utm_medium=aggregator&utm_campaign=symbol, https://www.digikey.ca/product-detail/en/murata-electronics-north-america/GRM1885C1H103JA01D/490-9666-1-ND/4934772?utm_source=snapeda&utm_medium=aggregator&utm_campaign=symbol, https://www.digikey.ca/product-detail/en/murata-electronics-north-america/GRM1885C1H103JA01D/490-9666-1-ND/4934772?utm_source=snapeda&utm_medium=aggregator&utm_campaign=symbol, https://www.digikey.ca/product-detail/en/murata-electronics-north-america/GRM1885C1H103JA01D/490-9666-1-ND/4934772?utm_source=snapeda&utm_medium=aggregator&utm_campaign=symbol, https://www.digikey.ca/product-detail/en/murata-electronics-north-america/GRM1885C1H103JA01D/490-9666-1-ND/4934772?utm_source=snapeda&utm_medium=aggregator&utm_campaign=symbol, https://www.digikey.ca/product-detail/en/murata-electronics-north-america/GRM1885C1H103JA01D/490-9666-1-ND/4934772?utm_source=snapeda&utm_medium=aggregator&utm_campaign=symbol, https://www.digikey.ca/product-detail/en/murata-electronics-north-america/GRM1885C1H103JA01D/490-9666-1-ND/4934772?utm_source=snapeda&utm_medium=aggregator&utm_campaign=symbol|GRM188R60G476ME15D, GRM188R60G476ME15D, GRM1885C1H103JA01D, GRM1885C1H103JA01D, GRM1885C1H103JA01D, GRM1885C1H103JA01D, GRM1885C1H103JA01D, GRM1885C1H103JA01D, GRM1885C1H103JA01D, GRM1885C1H103JA01D, GRM1885C1H103JA01D, GRM1885C1H103JA01D, GRM1885C1H103JA01D, GRM1885C1H103JA01D, GRM1885C1H103JA01D, GRM1885C1H103JA01D, GRM1885C1H103JA01D, GRM1885C1H103JA01D, GRM1885C1H103JA01D, GRM1885C1H103JA01D, GRM1885C1H103JA01D, GRM188R60G476ME15D, GRM188R60G476ME15D, GRM1885C1H103JA01D, GRM1885C1H103JA01D, GRM1885C1H103JA01D, GRM1885C1H103JA01D, GRM1885C1H103JA01D, GRM1885C1H103JA01D, GRM1885C1H103JA01D, GRM1885C1H103JA01D, GRM1885C1H103JA01D, GRM1885C1H103JA01D, GRM1885C1H103JA01D, GRM1885C1H103JA01D, GRM1885C1H103JA01D, GRM1885C1H103JA01D, GRM1885C1H103JA01D, GRM1885C1H103JA01D, GRM1885C1H103JA01D, GRM1885C1H103JA01D, GRM1885C1H103JA01D
8||GRM188R60J105KA01D
1||
1||
4||TPS75901KTTR
2||NCP705MTADJTCG
18|https://www.digikey.ca/product-detail/en/analog-devices-inc/ADUM210N1BRIZ/ADUM210N1BRIZ-ND/6072296|ADUM210N1BRIZ
1||
1||
4||RR0816P-513-D
8||RT0603BRD0730K1L, RT0603BRD0730K1L, RC0603FR-07130KL, ERJ-3GEY0R00V, RT0603BRD0730K1L, RT0603BRD0730K1L, RC0603FR-07130KL, ERJ-3GEY0R00V
1||
1||
1||

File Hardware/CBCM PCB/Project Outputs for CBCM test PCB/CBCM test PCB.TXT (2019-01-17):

M48
;Layer_Color=9474304
;FILE_FORMAT=2:5
INCH,TZ
;TYPE=PLATED
T1F00S00C0.01000
T2F00S00C0.02000
T3F00S00C0.02362
T4F00S00C0.02800
T5F00S00C0.03000
T6F00S00C0.03346
T7F00S00C0.03740
T8F00S00C0.03800
T9F00S00C0.05118
%
T01
X410000Y-45000
X425000
X440000
X455000
X470000
X485000
X500000
X515000
X530000
X545000
X560000
X575000
X590000
X605000
X620000
X635000
X650000
X665000
Y20000
X650000
X635000
X620000
X605000
X590000
X575000
X560000
X545000
X530000
X515000
X500000
X485000
X470000
X455000
X440000
X425000
X410000
X417500Y60500
X417000Y158000
X410000Y200000
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

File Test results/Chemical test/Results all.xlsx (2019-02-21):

W_alcohol0 | W_alcohol1 | W_alcohol2 | W_alcohol3 | W_alcohol4 | W_alcohol5 | W_alcohol6 | W_alcohol7 | WO_alcohol0 | WO_alcohol1 | WO_alcohol2 | WO_alcohol3 | WO_alcohol4 | WO_alcohol5 | WO_alcohol6 | WO_alcohol7 | WO_alcohol8 | WO_alcohol9 | WO_alcohol10 | WO_alcohol11 | W_flux0 | W_flux1 | W_flux2 | W_flux3 | WO_flux0 | WO_flux1 | W_cottonSwab0 | W_cottonSwab1 | W_cottonSwab2 | W_cottonSwab3 | W_cottonSwab4 | WO_cottonSwab0 | WO_cottonSwab1 | WO_cottonSwab2 | WO_cottonSwab3 | WO_cottonSwab4 | black tape | push with finger | push with tape
178.247 | 613.482 | 1169.89 | 2733.997 | 1424.848 | 175.982 | 1542.848 | 387.209 | 1085.235 | 1082.365 | 1082.85 | 1084.704 | 1079.988 | 1075.587 | 1075.87 | 1076.937 | 1079.481 | 1182.057 | 1077.264 | 1073.587 | 174.678 | 174.94 | 175.114 | 175.957 | 1114.918 | 1293.351 | 1080.899 | 1083.02 | 1081.755 | 1081.677 | 1083.211 | 1082.337 | 1079.616 | 1083.88 | 1079.961 | 1081.653 | 1076.415 | 1077.031 | 1076.584
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

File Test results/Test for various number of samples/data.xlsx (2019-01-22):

x1 | x10 | x100 | x1000 | x2000 | x3000 | x4000
16 | 801.2 | 813.11 | 797.703 | 797.703 | 799.6996667 | 799.60425
734 | 976.4 | 782.41 | 792.886 | 792.886 | 790.384 | 790.78125
789 | 1026.6 | 784.61 | 774.833 | 774.833 | 775.0556667 | 775.436
722 | 858.5 | 775.69 | 767.961 | 767.961 | 767.14 | 767.71925
727 | 999.7 | 759.13 | 742.41 | 742.41 | 743.2256667 | 742.63875
786 | 972.3 | 759.14 | 735.333 | 735.333 | 733.65 | 733.84175
730 | 956.4 | 750.46 | 720.392 | 720.392 | 719.5526667 | 719.43475
725 | 736.7 | 703.95 | 712.112 | 712.112 | 711.349 | 711.65
766 | 760.5 | 694.74 | 677.098 | 677.098 | 676.1156667 | 675.59475
675 | 798.4 | 682.29 | 667.664 | 667.664 | 666.797 | 667.03375
732 | 879.6 | 679.44 | 651.812 | 651.812 | 651.2253333 | 653.011
692 | 627 | 668.51 | 644.432 | 644.432 | 644.5686667 | 644.9495
696 | 778.4 | 651.95 | 622.627 | 622.627 | 621.4593333 | 621.09775
680 | 674.1 | 611.46 | 614.902 | 614.902 | 612.5036667 | 613.27
613 | 753.1 | 609.61 | 598.458 | 598.458 | 599.1206667 | 598.3985
569 | 558.9 | 585.22 | 593.199 | 593.199 | 590.8016667 | 591.46575
635 | 727.3 | 560.55 | 527.773 | 527.773 | 527.875 | 527.25775
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

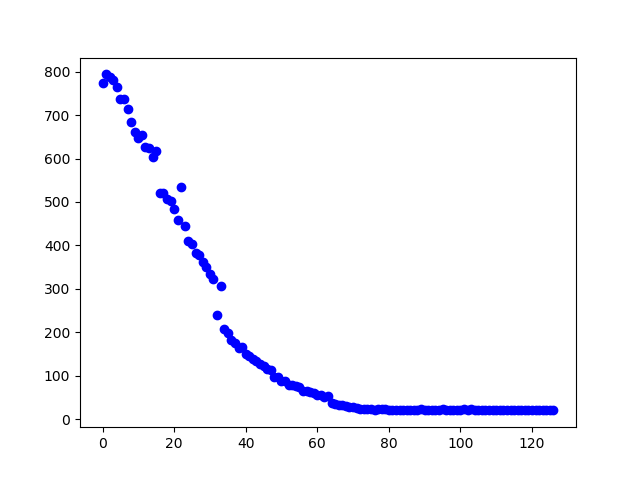
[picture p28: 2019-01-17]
Test results/Probe station test/close with glue 1.png

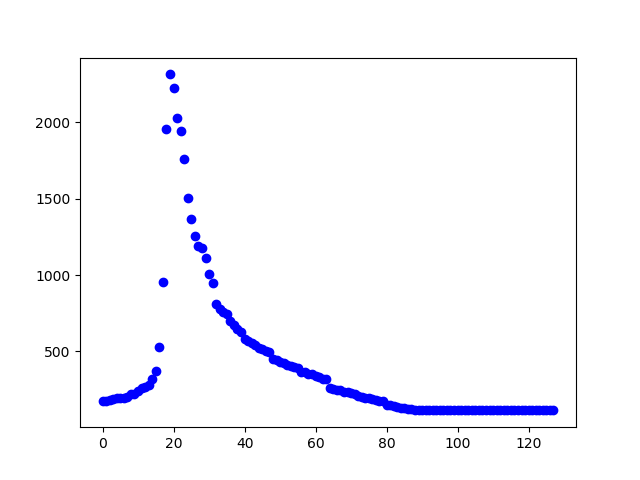
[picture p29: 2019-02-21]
Test results/Chemical test/02-19-2019 pre test/batch two/DI_water_3.png

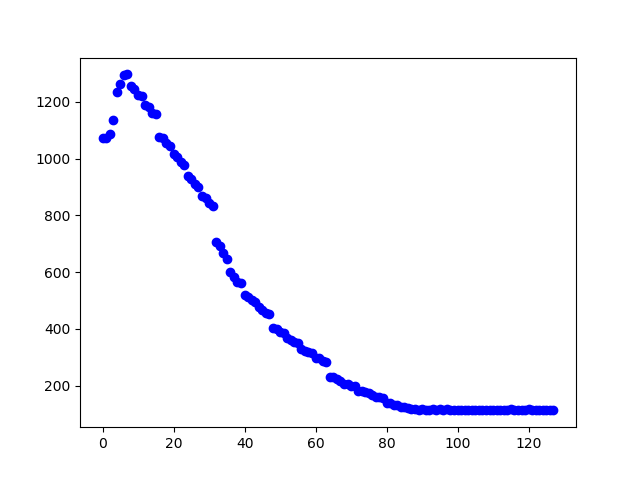
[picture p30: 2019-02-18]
Test results/Chemical test/02-15-2019/dry/WO_alcohol11.png

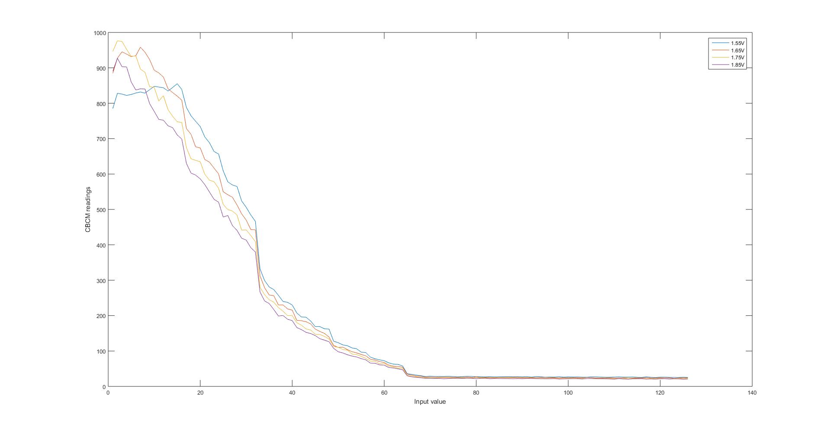
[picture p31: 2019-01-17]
Test results/Charactericzation tests/Test results 2/CCO voltage comparison.jpg

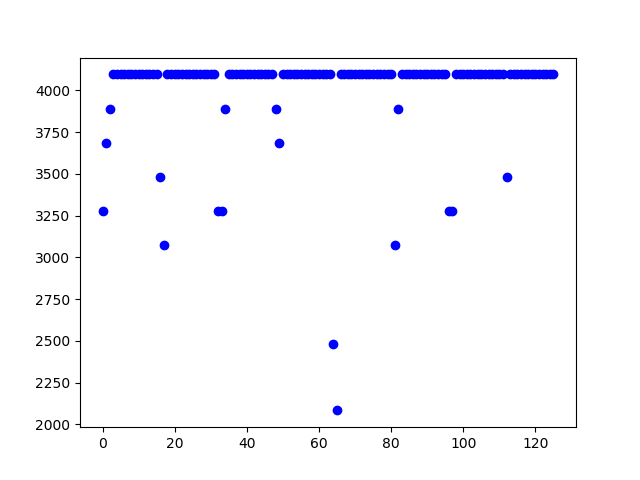
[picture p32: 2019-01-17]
Test results/Charactericzation tests/Test results 1/1.75V.png

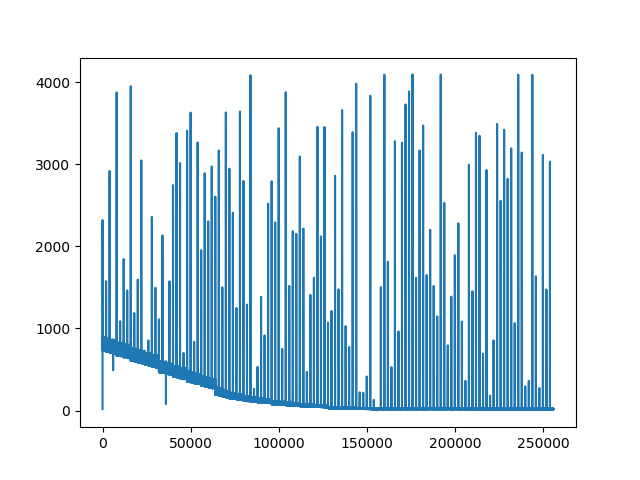
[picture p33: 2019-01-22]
Test results/Test for various number of samples/x2000 raw.png

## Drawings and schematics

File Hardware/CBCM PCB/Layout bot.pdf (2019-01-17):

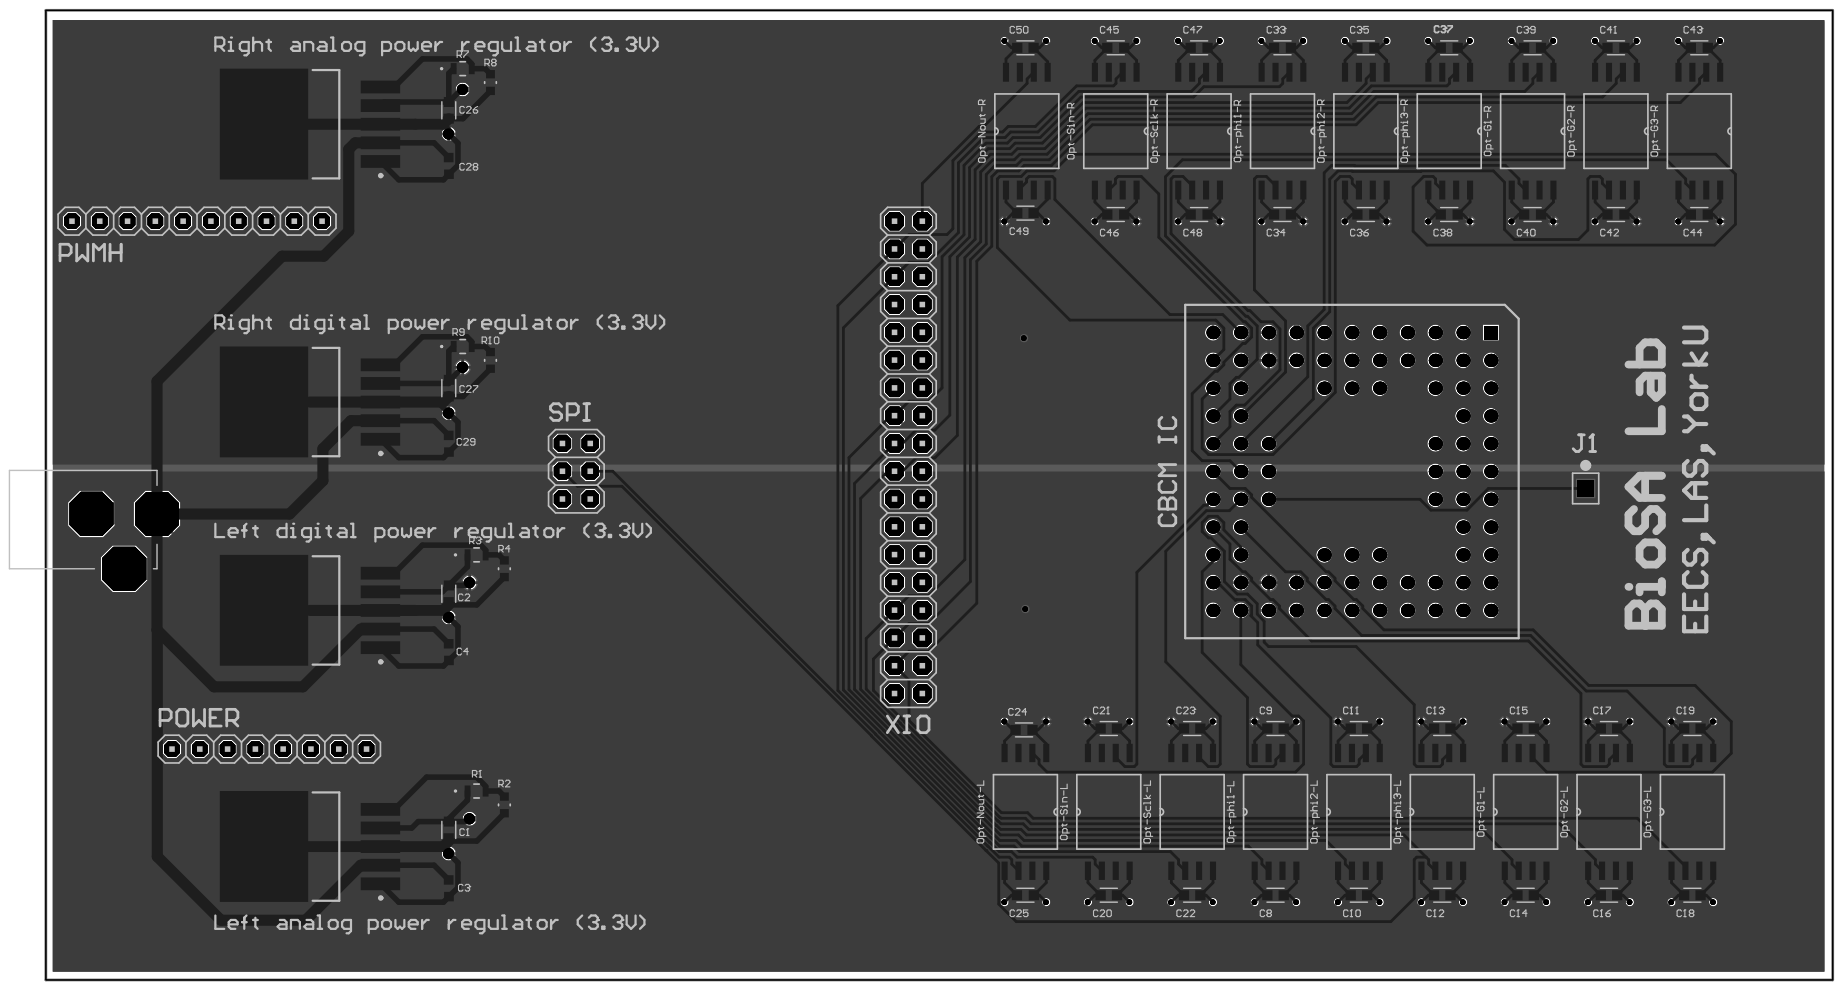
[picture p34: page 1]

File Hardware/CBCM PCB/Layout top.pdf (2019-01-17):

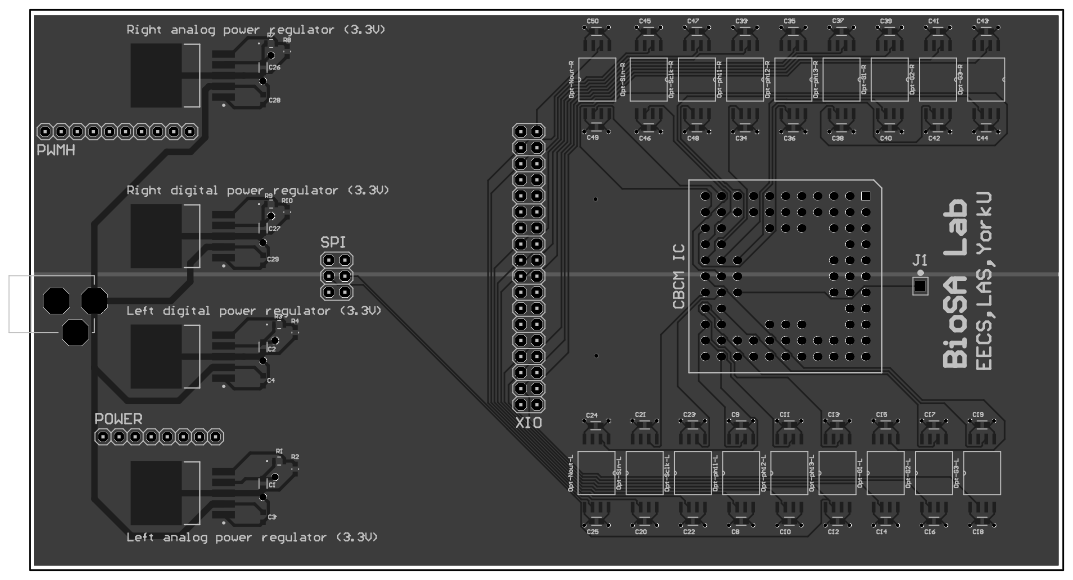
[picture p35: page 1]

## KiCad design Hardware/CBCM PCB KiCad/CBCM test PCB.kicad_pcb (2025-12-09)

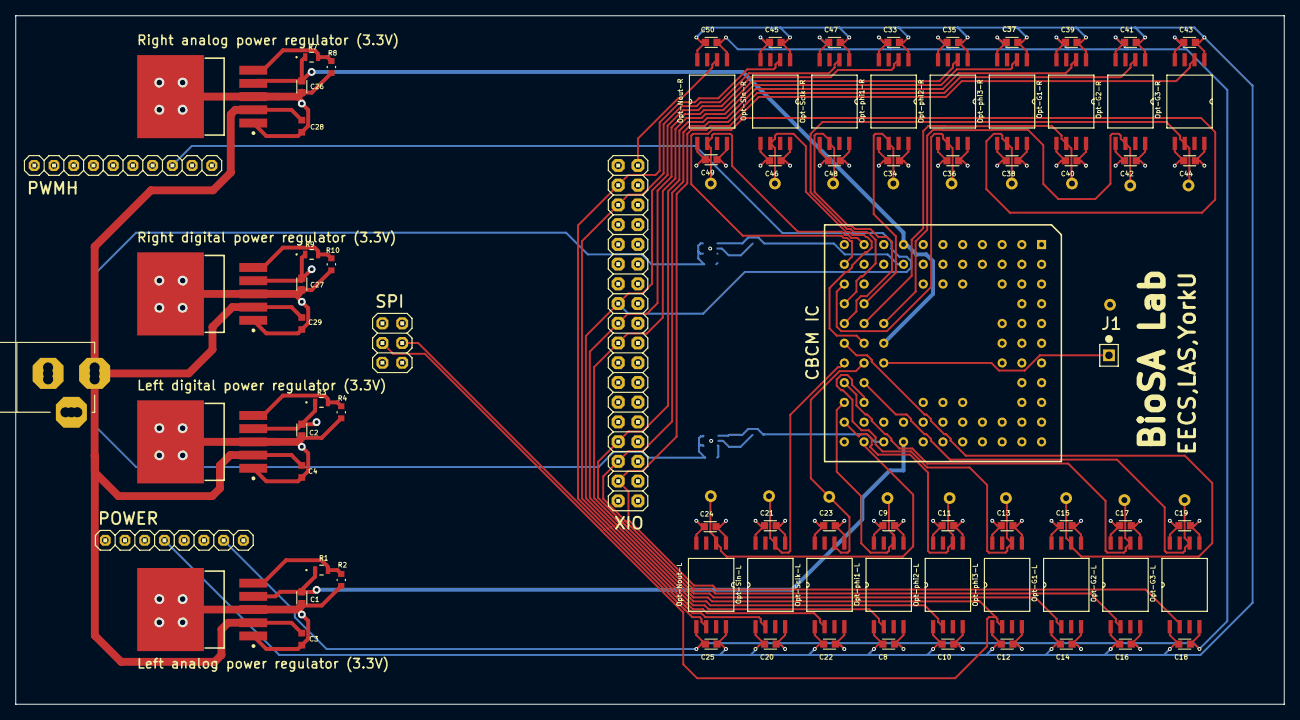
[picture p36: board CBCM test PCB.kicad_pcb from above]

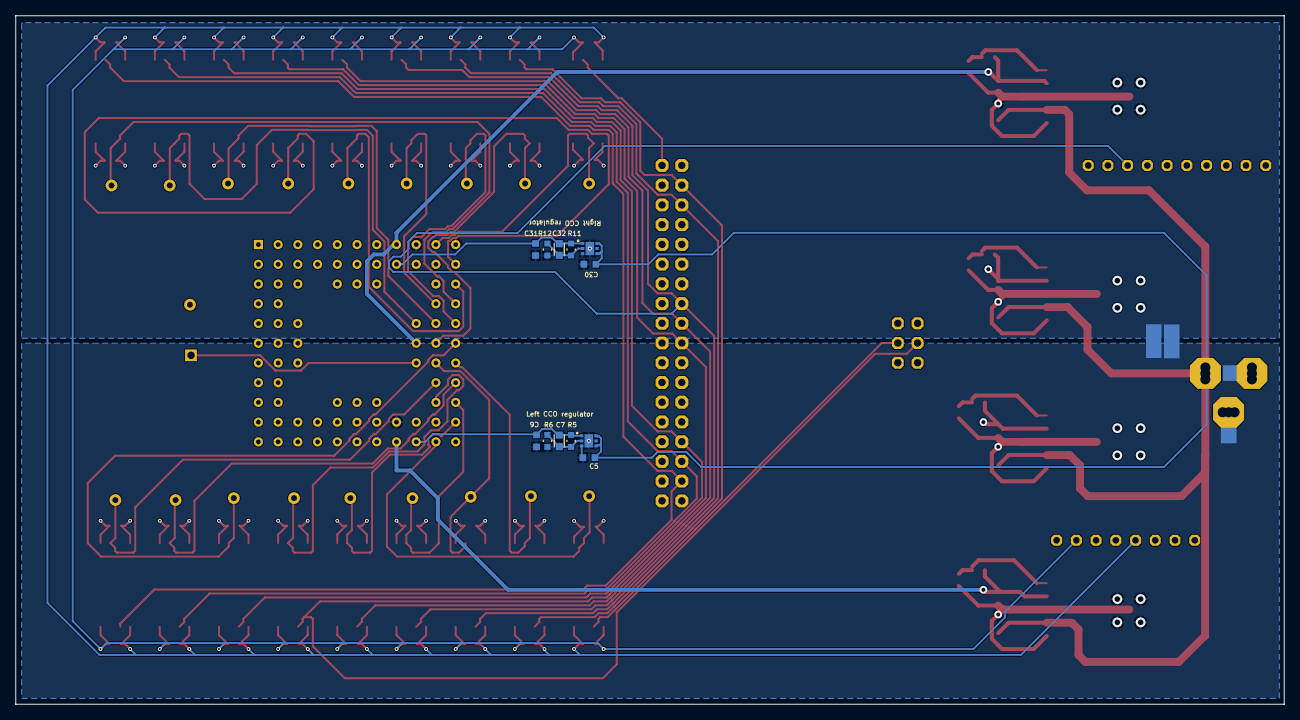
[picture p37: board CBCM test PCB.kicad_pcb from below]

Board: 4 copper layers, 163.3 x 88.6 mm, 99 parts (22 on the bottom side), 49 nets.

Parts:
C1, C2, C7, C8, C9, C10, C11, C12, C13, C14, C15, C16, C17, C18, C19, C20, C21, C22, C23, C24, C25, C26, C27, C32, C33, C34, C35, C36, C37, C38, C39, C40, C41, C42, C43, C44, C45, C46, C47, C48, C49, C50: C; CAPC1608X9N
C3, C4, C5, C6, C28, C29, C30, C31: C; CAP_GRM_188
CBCM IC: CBCM IC; PGA85x11
J1: 87224-1
Left CCO regulator: NCP705MTADJTCG; WDFN6
Left analog power regulator (3.3V): TPS75901KTTR; TO-263-5
Left digital power regulator (3.3V): TPS75901KTTR; TO-263-5
Opt-G1-L, Opt-G1-R, Opt-G2-L, Opt-G2-R, Opt-G3-L, Opt-G3-R: ADUM210N1BRIZ; SOIC127P1150X330-8N
Opt-Nout-L: ADUM210N1BRIZ; SOIC127P1150X330-8N
Opt-Nout-R: ADUM210N1BRIZ; SOIC127P1150X330-8N
Opt-Sclk-L: ADUM210N1BRIZ; SOIC127P1150X330-8N
Opt-Sclk-R: ADUM210N1BRIZ; SOIC127P1150X330-8N
Opt-Sin-L: ADUM210N1BRIZ; SOIC127P1150X330-8N
Opt-Sin-R: ADUM210N1BRIZ; SOIC127P1150X330-8N
Opt-phi1-L, Opt-phi1-R, Opt-phi2-L, Opt-phi2-R, Opt-phi3-L, Opt-phi3-R: ADUM210N1BRIZ; SOIC127P1150X330-8N
POWER: 8x1F-H8.5; 1X08
PWMH: 10x1F-H8.5; 1X10
R1, R3, R7, R9: R; RES_0816
R2, R4, R5, R6, R8, R10, R11, R12: R; RC0603N
Right CCO regulator: NCP705MTADJTCG; WDFN6
Right analog power regulator (3.3V): TPS75901KTTR; TO-263-5
Right digital power regulator (3.3V): TPS75901KTTR; TO-263-5
SPI: 3x2M; 2X03
X2: *; POWERSUPPLY_DC-21MM
XIO: 18x2F-H8.5; 2X18
tie1, tie2, tie3, tie4, tie5, tie6: Net Tie; net_tie

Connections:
+5: C3.2, C4.2, C5.2, C28.2, C29.2, C30.2, Left CCO regulator.4, Left CCO regulator.6, Left analog power regulator (3.3V).2, Left digital power regulator (3.3V).2, Right CCO regulator.4, Right CCO regulator.6, Right analog power regulator (3.3V).2, Right digital power regulator (3.3V).2, X2.2, X2.8, X2.9
D_GND: C2.1, C4.1, C9.2, C11.2, C13.2, C15.2, C17.2, C19.2, C21.2, C23.2, C24.2, C27.1, C29.1, C34.2, C36.2, C38.2, C40.2, C42.2, C44.2, C46.2, C48.2, C49.2, CBCM IC.K10, Left digital power regulator (3.3V).1, Left digital power regulator (3.3V).3, Left digital power regulator (3.3V).6, Opt-G1-L.5, Opt-G1-R.5, Opt-G2-L.5, Opt-G2-R.5, Opt-G3-L.5, Opt-G3-R.5, Opt-Nout-L.4, Opt-Nout-R.4, Opt-Sclk-L.5, Opt-Sclk-R.5, Opt-Sin-L.5, Opt-Sin-R.5, Opt-phi1-L.5, Opt-phi1-R.5, Opt-phi2-L.5, Opt-phi2-R.5, Opt-phi3-L.5, Opt-phi3-R.5, R4.2, R10.2, Right digital power regulator (3.3V).1, Right digital power regulator (3.3V).3, Right digital power regulator (3.3V).6, tie3.0, tie6.0
G1: Opt-G1-L.2, Opt-G1-R.2, XIO.29
G1-L: CBCM IC.L6, Opt-G1-L.6
G1-R: CBCM IC.K5, Opt-G1-R.6
G2: Opt-G2-L.2, Opt-G2-R.2, XIO.31
G2-L: CBCM IC.L8, Opt-G2-L.6
G2-R: CBCM IC.J5, Opt-G2-R.6
G3: Opt-G3-L.2, Opt-G3-R.2, XIO.33
G3-L: CBCM IC.K8, Opt-G3-L.6
G3-R: CBCM IC.L4, Opt-G3-R.6
LA_3.3: C1.2, CBCM IC.H11, Left analog power regulator (3.3V).4, R1.1
LA_GND: C1.1, C3.1, C5.1, C6.1, CBCM IC.H10, Left CCO regulator.3, Left CCO regulator.GND, Left analog power regulator (3.3V).1, Left analog power regulator (3.3V).3, Left analog power regulator (3.3V).6, R2.2, R6.2, tie1.0, tie2.1, tie4.1, tie5.0
LCCO_1.85V: C6.2, C7.1, CBCM IC.J11, Left CCO regulator.1, R5.1
LD_3.3: C2.2, C9.1, C11.1, C13.1, C15.1, C17.1, C19.1, C21.1, C23.1, C24.1, CBCM IC.J10, Left digital power regulator (3.3V).4, Opt-G1-L.8, Opt-G2-L.8, Opt-G3-L.8, Opt-Nout-L.1, Opt-Sclk-L.8, Opt-Sin-L.8, Opt-phi1-L.8, Opt-phi2-L.8, Opt-phi3-L.8, R3.1
NOUT: Opt-Nout-L.6, SPI.4
NOUT-L: CBCM IC.K11, Opt-Nout-L.2
NOUT-R: CBCM IC.K1, Opt-Nout-R.2
NOUT_TEST: Opt-Nout-R.6, XIO.2
NetC7_2: C7.2, Left CCO regulator.2, R5.2, R6.1
NetC32_2: C32.2, R11.2, R12.1, Right CCO regulator.2
NetCBCM IC_33: CBCM IC.J7, J1.1
NetLeft analog power regulator (3.3V)_5: Left analog power regulator (3.3V).5, R1.2, R2.1
NetLeft digital power regulator (3.3V)_5: Left digital power regulator (3.3V).5, R3.2, R4.1
NetR7_2: R7.2, R8.1, Right analog power regulator (3.3V).5
NetR9_2: R9.2, R10.1, Right digital power regulator (3.3V).5
Nettie1_1: X2.1, X2.4, X2.5, tie1.1, tie3.1
Nettie4_0: X2.3, X2.6, X2.7, tie4.0, tie6.1
PHI1: Opt-phi1-L.2, Opt-phi1-R.2, PWMH.3, XIO.15
PHI1-L: CBCM IC.L9, Opt-phi1-L.6
PHI1-R: CBCM IC.K4, Opt-phi1-R.6
PHI2: Opt-phi2-L.2, Opt-phi2-R.2, XIO.17
PHI2-L: CBCM IC.L10, Opt-phi2-L.6
PHI2-R: CBCM IC.L3, Opt-phi2-R.6
PHI3: Opt-phi3-L.2, Opt-phi3-R.2, SPI.3, XIO.19
PHI3-L: CBCM IC.K9, Opt-phi3-L.6
PHI3-R: CBCM IC.L2, Opt-phi3-R.6
RA_3.3: C26.2, CBCM IC.H1, CBCM IC.J6, R7.1, Right analog power regulator (3.3V).4
RA_GND: C26.1, C28.1, C30.1, C31.1, CBCM IC.J1, CBCM IC.L1, R8.2, R12.2, Right CCO regulator.3, Right CCO regulator.GND, Right analog power regulator (3.3V).1, Right analog power regulator (3.3V).3, Right analog power regulator (3.3V).6, tie2.0, tie5.1
RCCO_1.85V: C31.2, C32.1, CBCM IC.H2, R11.1, Right CCO regulator.1
RD_3.3: C27.2, C34.1, C36.1, C38.1, C40.1, C42.1, C44.1, C46.1, C48.1, C49.1, CBCM IC.J2, Opt-G1-R.8, Opt-G2-R.8, Opt-G3-R.8, Opt-Nout-R.1, Opt-Sclk-R.8, Opt-Sin-R.8, Opt-phi1-R.8, Opt-phi2-R.8, Opt-phi3-R.8, R9.1, Right digital power regulator (3.3V).4
SCLK: Opt-Sclk-L.2, Opt-Sclk-R.2, XIO.5
SCLK-L: CBCM IC.K7, Opt-Sclk-L.6
SCLK-R: CBCM IC.L5, Opt-Sclk-R.6
SIN: Opt-Sin-L.2, Opt-Sin-R.2, XIO.3
SIN-L: CBCM IC.L7, Opt-Sin-L.6
SIN-R: CBCM IC.K6, Opt-Sin-R.6
UC_3.3: C8.1, C10.1, C12.1, C14.1, C16.1, C18.1, C20.1, C22.1, C25.1, C33.1, C35.1, C37.1, C39.1, C41.1, C43.1, C45.1, C47.1, C50.1, Opt-G1-L.1, Opt-G1-R.1, Opt-G2-L.1, Opt-G2-R.1, Opt-G3-L.1, Opt-G3-R.1, Opt-Nout-L.8, Opt-Nout-R.8, Opt-Sclk-L.1, Opt-Sclk-R.1, Opt-Sin-L.1, Opt-Sin-R.1, Opt-phi1-L.1, Opt-phi1-R.1, Opt-phi2-L.1, Opt-phi2-R.1, Opt-phi3-L.1, Opt-phi3-R.1, POWER.4
UC_GND: C8.2, C10.2, C12.2, C14.2, C16.2, C18.2, C20.2, C22.2, C25.2, C33.2, C35.2, C37.2, C39.2, C41.2, C43.2, C45.2, C47.2, C50.2, Opt-G1-L.4, Opt-G1-R.4, Opt-G2-L.4, Opt-G2-R.4, Opt-G3-L.4, Opt-G3-R.4, Opt-Nout-L.5, Opt-Nout-R.5, Opt-Sclk-L.4, Opt-Sclk-R.4, Opt-Sin-L.4, Opt-Sin-R.4, Opt-phi1-L.4, Opt-phi1-R.4, Opt-phi2-L.4, Opt-phi2-R.4, Opt-phi3-L.4, Opt-phi3-R.4, POWER.6, POWER.7, SPI.6, XIO.35, XIO.36

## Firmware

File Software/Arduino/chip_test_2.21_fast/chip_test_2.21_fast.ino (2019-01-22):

short result = 0;
int N_sample = 1000;

void setup() {
  Serial.begin(115200);
  
  // put your setup code here, to run once:
  REG_PMC_PCER1 |= PMC_PCER1_PID36;// Power up PWM clock
  REG_PWM_WPCR = PWM_WPCR_WPCMD(0);//Unlock user interface for PWM
  REG_PWM_CLK = PWM_CLK_PREA(0)|PWM_CLK_DIVA(21); //config the PWM clock generator: clock A, 84/21 = 4MHz
  REG_PWM_SCM = PWM_SCM_SYNC0|PWM_SCM_SYNC1;//Synchronize phi1 and phi2 for they have the same frequency
   
  //config phi1, Output pin PC2, Digital pin 34
  REG_PIOC_ABSR |= PIO_ABSR_P2; // Transfer Pin control from PIO to PWM
  REG_PIOC_PDR |= PIO_PDR_P2;   // Set PWM pin to an output
  REG_PWM_CMR0 = PWM_CMR_CPRE_CLKA; //mode congiration for channel 0: clock A, letft aligned, waveform start at high
  REG_PWM_CPRD0 = PWM_CPRD_CPRD(60);//config period for pwm 60/(4MHz)
  REG_PWM_CDTY0 = PWM_CDTY_CDTY(16);// 80/3% duty cycle
  REG_PWM_ENA = PWM_ENA_CHID0;// enable PWM channel0
  
  //config phi2, Output pin PC4, Digital pin 36
  REG_PIOC_ABSR |= PIO_ABSR_P4; // Transfer Pin control from PIO to PWM
  REG_PIOC_PDR |= PIO_PDR_P4;   // Set PWM pin to an output
  REG_PWM_CMR1 = PWM_CMR_CPRE_CLKA|PWM_CMR_DTE; //mode congiration for channel 0: clock A, letft aligned, waveform start at high
  REG_PWM_CPRD1 = PWM_CPRD_CPRD(60);//config period for pwm 60/(4MHz)
  REG_PWM_DT1 = PWM_DT_DTL(4); //create the 1us(delay)
  REG_PWM_CDTY1 = PWM_CDTY_CDTY(12);// 80/3% duty cycle
  REG_PWM_ENA = PWM_ENA_CHID1;// enable PWM channel1
  
  //config phi3, Output pin PC6, Digital pin 38
  REG_PIOC_ABSR |= PIO_ABSR_P6; // Transfer Pin control from PIO to PWM
  REG_PIOC_PDR |= PIO_PDR_P6;   // Set PWM pin to an output
  REG_PWM_CMR2 = PWM_CMR_CPRE_CLKA;//mode congiration for channel 0: clock A, letft aligned, waveform start at low
  REG_PWM_CPRD2 = PWM_CPRD_CPRD(2);//config period for pwm 2/(4MHz)
  REG_PWM_CDTY2 = PWM_CDTY_CDTY(1);//50% duty cycle
  REG_PWM_ENA = PWM_ENA_CHID2;// enable PWM channel2
  
  //SPI serial recieve 
  REG_PMC_PCER0 |= PMC_PCER0_PID24;// Power up SPI clock
  REG_SPI0_WPMR = 0<<SPI_WPMR_WPEN;//Unlock user interface for SPI
  
  //Instance SPI0, MISO: PA25, (MISO), MOSI: PA26, (MOSI), SCLK: PA27, (SCLK), NSS: PA28, Digital pin 10 
  REG_PIOA_ABSR |= PIO_ABSR_P25; // Transfer Pin control from PIO to SPI
  REG_PIOA_PDR |= PIO_PDR_P25;   // Set MISO pin to an output

  REG_PIOA_ABSR |= PIO_ABSR_P26; // Transfer Pin control from PIO to SPI
  REG_PIOA_PDR |= 0<<PIO_PDR_P26;   // Set MOSI pin to an input

  REG_PIOA_ABSR |= PIO_ABSR_P27; // Transfer Pin control from PIO to SPI
  REG_PIOA_PDR |= 0<<PIO_PDR_P27;   // Set SCLK pin to an input

  REG_PIOA_ABSR |= PIO_ABSR_P28; // Transfer Pin control from PIO to SPI
  REG_PIOA_PDR |= 0<<PIO_PDR_P28;   // Set NSS pin to an input

  //REG_ISER0 = 1<<24; //Enable interrupt controller
  REG_SPI0_CR = 1; // Enable SPI
  REG_SPI0_MR = 0; // Slave mode  
  REG_SPI0_IER = 1<<SPI_IER_RDRF|1<<SPI_IER_OVRES|1<<SPI_IER_NSSR; //Enable interrupts
  SPI0->SPI_CSR[0] = SPI_CSR_BITS_12_BIT; // Capture on falling edge and transfer 12 bits.

  pinMode(22,OUTPUT);// Sin
  pinMode(24,OUTPUT);// Sclk
  pinMode(48,OUTPUT);//G1
  pinMode(50,OUTPUT);//G2
  pinMode(52,OUTPUT);//G3
  digitalWrite(48,HIGH);
  digitalWrite(50,HIGH);
  digitalWrite(52,HIGH);
  delay(100);
  digitalWrite(22, LOW);
  digitalWrite(24, LOW);  
  //inputSig("00010011"); 
  digitalWrite(22, LOW);
  digitalWrite(24, LOW); 
  delay(10);
}

void inputSig(char testSeq[])
{
  //turn off the phi clock pulses
  REG_PWM_DIS = PWM_DIS_CHID0;
  REG_PWM_DIS = PWM_DIS_CHID1;
  REG_PWM_DIS = PWM_DIS_CHID2;
  delayMicroseconds(1);
  //fully reset the input registers
  for(int i = 13; i>0 ;i--)
  {
     digitalWrite(22, LOW);
     digitalWrite(24, LOW);
     delay(1);      
     digitalWrite(24,HIGH);
     delay(1);
  }
  //apply input sequences
  for(int i = 0; i<7 ;i++)
  {
    if(testSeq[i] == '0')
    {
      digitalWrite(22, LOW);
      digitalWrite(24, LOW);
      delay(1);      
      digitalWrite(24,HIGH);
      delay(1);
    }  
    else if(testSeq[i] == '1')
    {
      digitalWrite(22, HIGH);
      digitalWrite(24, LOW);
      delay(1);      
      digitalWrite(24,HIGH);
      delay(1);
    }
  }
  delayMicroseconds(1);
  digitalWrite(22, LOW);
  digitalWrite(24, LOW);
  //turn the phi pulses back on
  REG_PWM_ENA = PWM_ENA_CHID0;
  REG_PWM_ENA = PWM_ENA_CHID1;
  REG_PWM_CMR2 = 0;
  REG_PWM_CMR2 = PWM_CMR_CPRE_CLKA;
  REG_PWM_CMR2 &= ~PWM_CMR_CPOL;
  REG_PWM_ENA = PWM_ENA_CHID2;
}

void loop() {
  //inputSig("11101010"); 
  char calin_i[7];
  //Serial.println(1);
  if(Serial.available()>0)
  {
    //Serial.println(2);
    char temp = Serial.read();
    switch (temp)
    {
      case 'S':   
        for(int i = 0; i<4; )
        {
          if(Serial.available() > 0) 
          {      
            calin_i[i] = Serial.read();
            i++;
          }
        }
        calin_i[4] = '\0';
        N_sample = atoi(calin_i);
        //Serial.println(calin_i); 
        Serial.println(N_sample); 
        break;
      case 'W':
        for(int i = 0; i<7; )
        {
          if(Serial.available() > 0) 
          {      
            calin_i[i] = Serial.read();
            i++;
          }
        }
        inputSig(calin_i);
        break;
      case 'G':
        for(int i = 0; i<3; )
        {
          if(Serial.available() > 0) 
          {      
            calin_i[i] = Serial.read();
            i++;
          }
          if(calin_i[i] == '1')
            digitalWrite(48+i,HIGH);
          else
            digitalWrite(48+i,LOW);
        }
        break;
      case 'R':
        unsigned char buf[N_sample*sizeof(short)];
        for(int i = 0;i<N_sample;)
        {
          if(REG_SPI0_SR&1)
          {
            result = REG_SPI0_RDR;  
            buf[2*i] = highByte(result);
            buf[2*i+1] = lowByte(result); 
            i++;
           }    
        } 
        delay(1);
        Serial.write(buf,N_sample*sizeof(short)); 
        Serial.flush();
        break;
       default:
        Serial.println('\0');
        break;       
    }
     
  }
  
}

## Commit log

2019-01-17 Initail commit on github
    Read out software is able to take 1000+ samples per calibration point
    [1.45V.csv, 1.4V.csv, 1.50V.csv, 1.55V.csv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]
2019-01-22 Sample number change and hydro gel test results
    1) Added option to change the number of samples.
    2) Added testing result with hydro gels
    [CT_records.csv, CT_results.csv, Hydro gel avg.csv, Hydro gel avg2.csv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]
2019-02-13 Generated python GUI code
    Task to be done:
    1) display debug message in the Qtext browser.
    2) implement all button handlers
    3) integrate graph window(optional)
    [CT_records.csv, CT_results.csv, ST_records.csv]
2019-02-14 GUI working with minor bugs
    1) feed back on the sample change incorrect(actual number of sample written to the microcontroller is correct)
    2)need to implement automactic port closure on exit
    3)need to implement feed back of CCO resolution
    4) disable all buttons when port is occupied.
    [CT_records.csv, CT_results.csv, ST_records.csv]
2019-02-18 GUI fully functional, chemical tests added
    potential improvements:
    add a new thread for calibraiton scan.
    add a welcome message and instructions in the text browser.
    [CT_records.csv, CT_results.csv, ST_records.csv, WO_alcohol0.csv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]
2019-02-21 02-20-2019 chemical test results
    [Aceton_0.csv, CT_records.csv, CT_results.csv, DI_water_0.csv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]
2019-04-04 real time data streaming (unfinished)
    graph does not auto update:
    1) might because a lack of auto updating time axis
    2) the loop is not running
    program cashs after clicking stop button
    [CT_records.csv, CT_results.csv, ST_records.csv]
2019-04-12 Real time monitoring of a single calibration value
    Things are done:
    Real time monitoring of a single calibration value functional
    Things to be done:
    1) Keep the plot window paused on hitting the stop button
    2) Add spectrum analysis, multiple continuous calibration value scan
    3) Add default value for parameter settings
    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
    [ST_records.csv]
2019-04-18 Spectrum analysis done
    To be done:
    2) Add default value for parameter settings
    3) Add welcome message and usage instructions in the text area on start up
    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
    [CT_records.csv, CT_results.csv]
2019-05-10 Fixing the average value bug
    [CT_records.csv, CT_results.csv, ST_records.csv]
2019-06-13 Fix the bug that input dosen't include the mode swap bit
    Fix the bug that input dosen't include the mode swap bit
    Now input has 8 bits, the additional bit swaps the chip between calibration mode and sensing mode.
2019-06-21 Fix a bug where arduino is not returning input values
    [CT_records.csv, CT_results.csv, ST_records.csv]
2019-07-05 Final test version(messy need reorganize)
    1) The final version of both arduino and GUI code are in the -copy folder
    2) Final test result proving the spikes on the right side are a result of oscillator behavior
    [CT_records.csv, CT_results.csv, ST_records.csv]
2019-09-05 Started designs on CBCMmin PCB
    [1Mhz left res000 samp100.csv, 1Mhz left res000 samp1000.csv, 1Mhz left res111 samp100.csv, 1Mhz left res111 samp1000.csv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]
2025-12-09 Add photo and Kicad version of the design
    [CBCM PCB Rev 1.kicad_pcb, CBCM test PCB.kicad_pcb, CBCM test PCB.kicad_sch, IC common.kicad_sch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]
2025-12-09 update Readme (私とココの将来のために)
2025-12-10 Add photos of the project.
    [CBCM PCB Rev 1.kicad_pcb, CT_records.csv, CT_results.csv, ST_records.csv]

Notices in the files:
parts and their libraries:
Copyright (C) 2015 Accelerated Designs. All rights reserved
